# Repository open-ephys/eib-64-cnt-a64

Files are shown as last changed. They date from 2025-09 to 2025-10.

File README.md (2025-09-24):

# EIB for CNT A64 probes

- 64 electrodes
- Power ground (GND), amplifier reference (REF), VCoax, LED Cathode 0 and 1, and I-stim signals exposed via 2.54mm header
- Compatible with:
  - [Low Profile SPI](https://open-ephys.org/acquisition-system/oeps-6570-6571)
  - [headstage-64](https://open-ephys.org/onix/oeps-7741)

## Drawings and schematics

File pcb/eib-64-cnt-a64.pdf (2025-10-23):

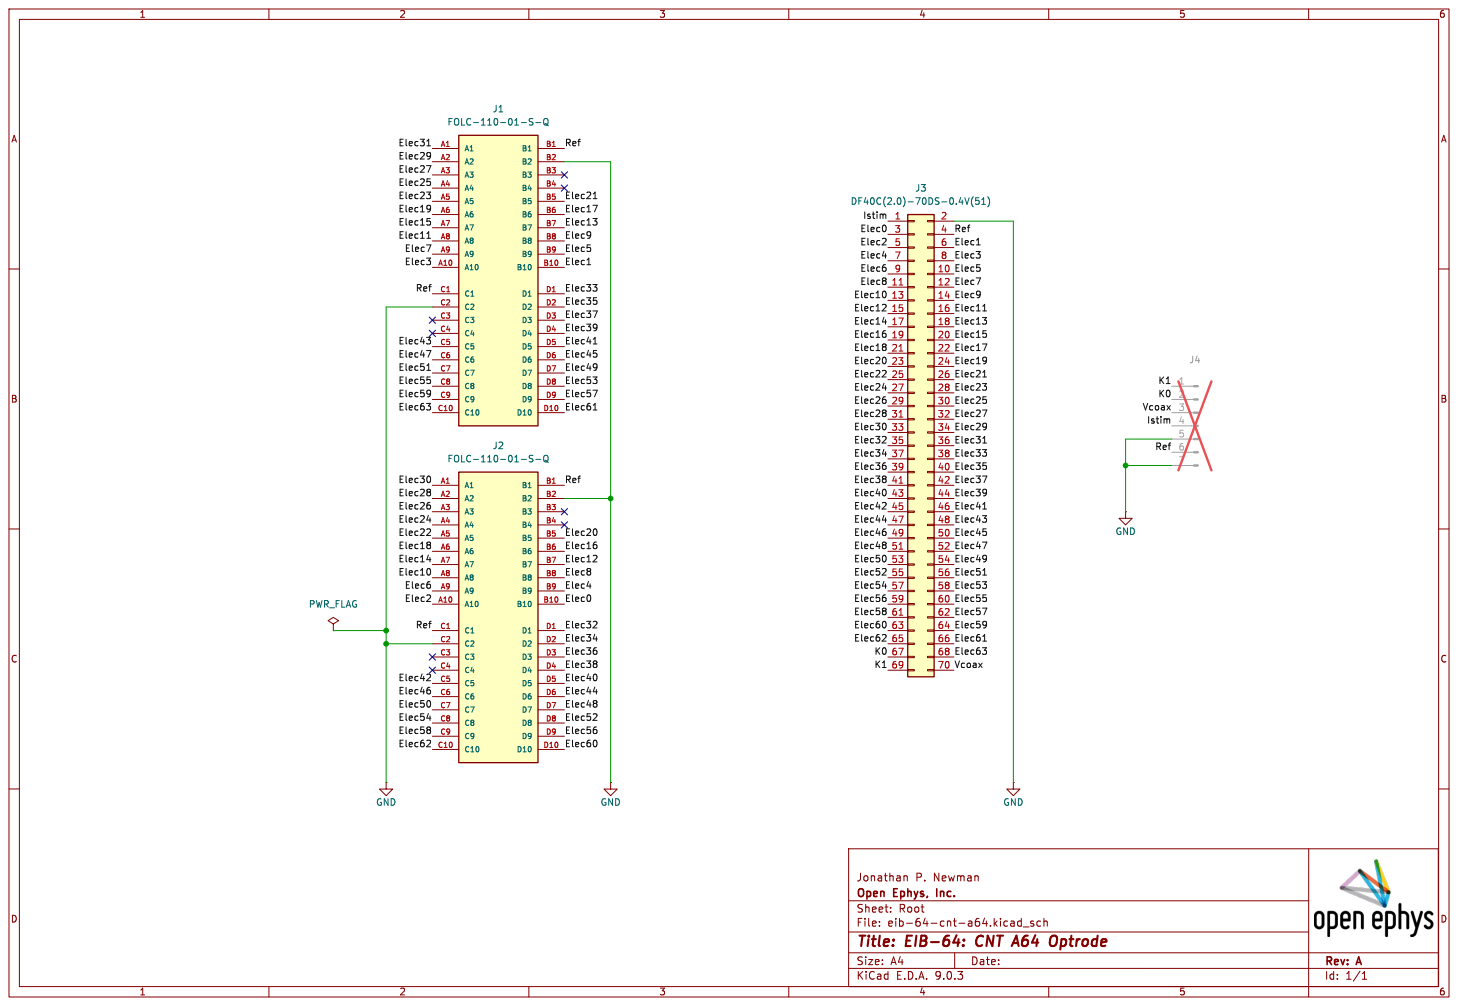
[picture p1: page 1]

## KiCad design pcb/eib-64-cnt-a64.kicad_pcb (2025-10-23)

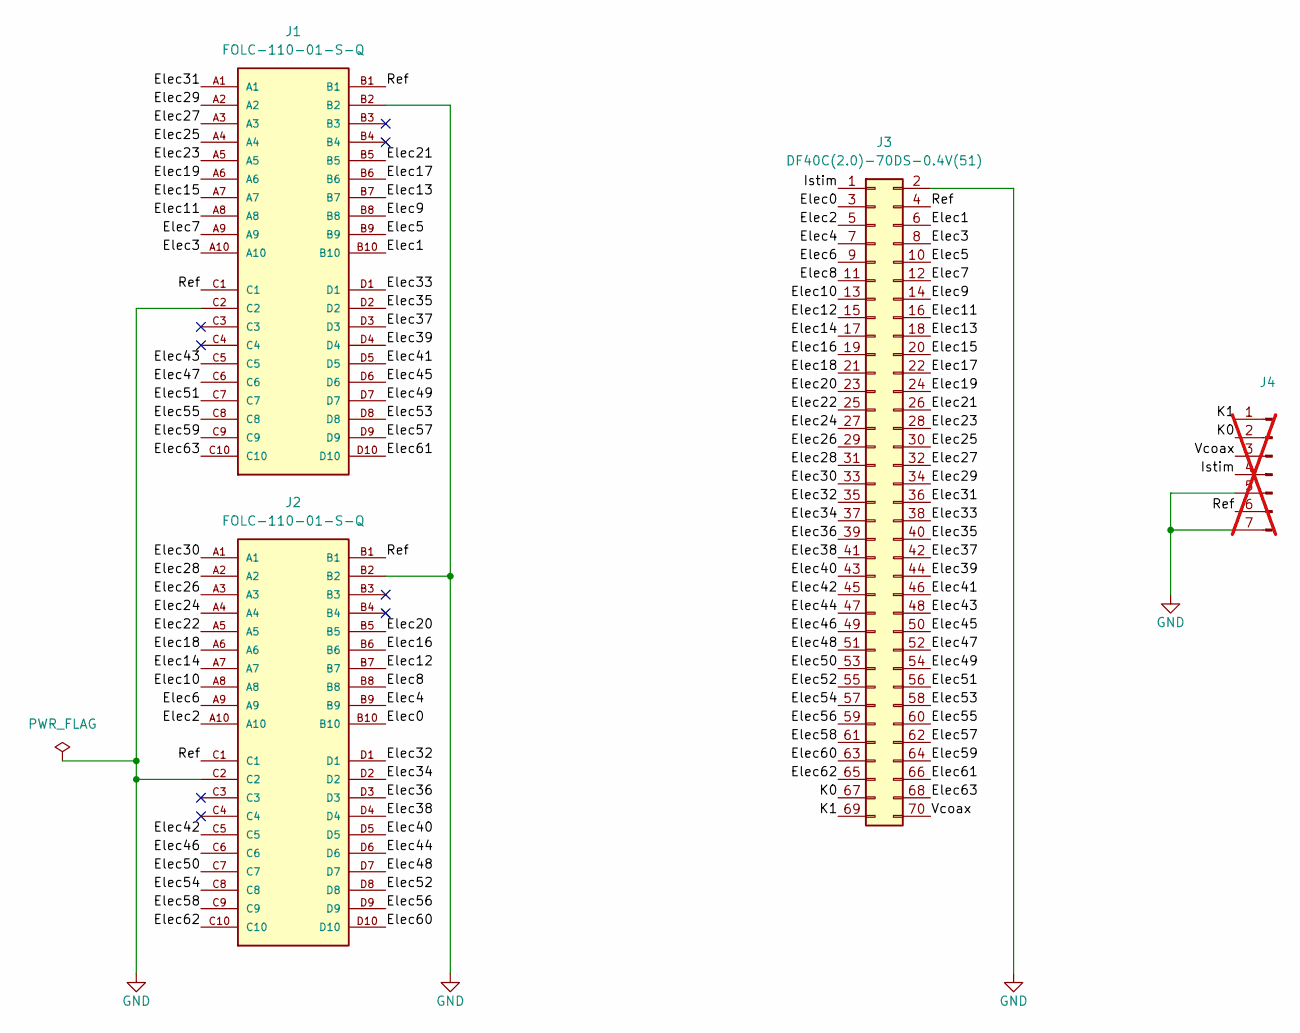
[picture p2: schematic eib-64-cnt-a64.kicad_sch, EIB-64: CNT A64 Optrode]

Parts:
J1, J2: FOLC-110-01-S-Q; SAMTEC_FOLC-110-01-S-Q
J3: DF40C(2.0)-70DS-0.4V(51); HIROSE_DF40C(2.0)-70DS-0.4V(51)
J4: Conn_01x07_Male; PinHeader_1x07_P2.54mm_Vertical; not fitted

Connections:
/Elec0: J2.B10, J3.3
/Elec1: J1.B10, J3.6
/Elec2: J2.A10, J3.5
/Elec3: J1.A10, J3.8
/Elec4: J2.B9, J3.7
/Elec5: J1.B9, J3.10
/Elec6: J2.A9, J3.9
/Elec7: J1.A9, J3.12
/Elec8: J2.B8, J3.11
/Elec9: J1.B8, J3.14
/Elec10: J2.A8, J3.13
/Elec11: J1.A8, J3.16
/Elec12: J2.B7, J3.15
/Elec13: J1.B7, J3.18
/Elec14: J2.A7, J3.17
/Elec15: J1.A7, J3.20
/Elec16: J2.B6, J3.19
/Elec17: J1.B6, J3.22
/Elec18: J2.A6, J3.21
/Elec19: J1.A6, J3.24
/Elec20: J2.B5, J3.23
/Elec21: J1.B5, J3.26
/Elec22: J2.A5, J3.25
/Elec23: J1.A5, J3.28
/Elec24: J2.A4, J3.27
/Elec25: J1.A4, J3.30
/Elec26: J2.A3, J3.29
/Elec27: J1.A3, J3.32
/Elec28: J2.A2, J3.31
/Elec29: J1.A2, J3.34
/Elec30: J2.A1, J3.33
/Elec31: J1.A1, J3.36
/Elec32: J2.D1, J3.35
/Elec33: J1.D1, J3.38
/Elec34: J2.D2, J3.37
/Elec35: J1.D2, J3.40
/Elec36: J2.D3, J3.39
/Elec37: J1.D3, J3.42
/Elec38: J2.D4, J3.41
/Elec39: J1.D4, J3.44
/Elec40: J2.D5, J3.43
/Elec41: J1.D5, J3.46
/Elec42: J2.C5, J3.45
/Elec43: J1.C5, J3.48
/Elec44: J2.D6, J3.47
/Elec45: J1.D6, J3.50
/Elec46: J2.C6, J3.49
/Elec47: J1.C6, J3.52
/Elec48: J2.D7, J3.51
/Elec49: J1.D7, J3.54
/Elec50: J2.C7, J3.53
/Elec51: J1.C7, J3.56
/Elec52: J2.D8, J3.55
/Elec53: J1.D8, J3.58
/Elec54: J2.C8, J3.57
/Elec55: J1.C8, J3.60
/Elec56: J2.D9, J3.59
/Elec57: J1.D9, J3.62
/Elec58: J2.C9, J3.61
/Elec59: J1.C9, J3.64
/Elec60: J2.D10, J3.63
/Elec61: J1.D10, J3.66
/Elec62: J2.C10, J3.65
/Elec63: J1.C10, J3.68
/Istim: J3.1, J4.4
/K0: J3.67, J4.2
/K1: J3.69, J4.1
/Ref: J1.B1, J1.C1, J2.B1, J2.C1, J3.4, J4.6
/Vcoax: J3.70, J4.3
GND: J1.B2, J1.C2, J2.B2, J2.C2, J3.2, J4.5, J4.7

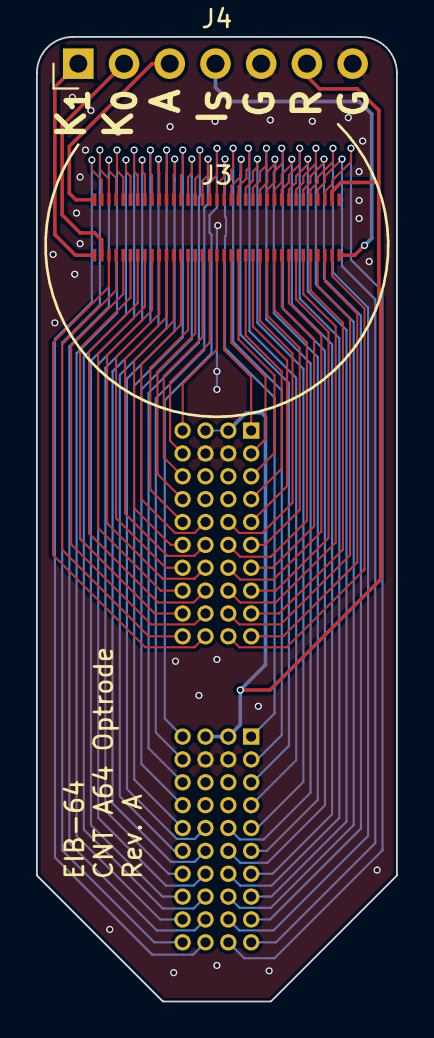
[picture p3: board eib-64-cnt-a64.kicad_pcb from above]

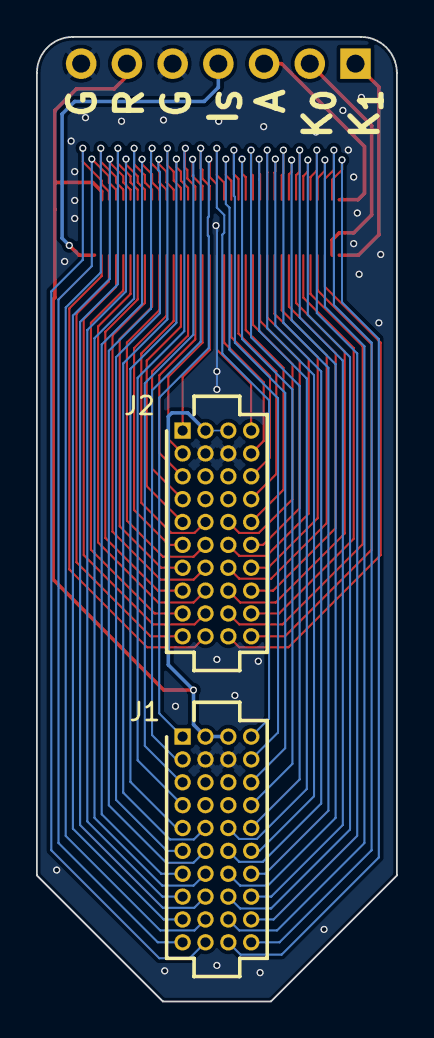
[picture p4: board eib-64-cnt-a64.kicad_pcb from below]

Board: 4 copper layers, 20.0 x 53.6 mm, 4 parts (2 on the bottom side), 70 nets.

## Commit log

2025-09-24 Initial commit
    - Rev. A inital design
    [eib-64-cnt-a64-B_Cu.gbr, eib-64-cnt-a64-B_Fab.gbr, eib-64-cnt-a64-B_Mask.gbr, eib-64-cnt-a64-B_Paste.gbr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]
2025-09-30 Revision A
    - Set to JLC for production
    [eib-64-cnt-a64-B_Cu.gbr, eib-64-cnt-a64-B_Fab.gbr, eib-64-cnt-a64-B_Mask.gbr, eib-64-cnt-a64-B_Paste.gbr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]
2025-10-23 Revision A
    - This was fabricated and tested.
    [eib-64-cnt-a64.kicad_pcb, eib-64-cnt-a64.kicad_sch]
